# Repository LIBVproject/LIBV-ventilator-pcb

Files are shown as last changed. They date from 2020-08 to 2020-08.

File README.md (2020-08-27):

# LIBV Open Source Ventilator

Check out our [www.bvmvent.org](https://www.bvmvent.org/) for updates.

**The Problem:** The COVID-19 Pandemic has highlighted the scarcity of potentially life-saving resources around the world.

**Our Challenge:** Design and Engineer an Open Source, low cost (sub $150) ventilator using readily available materials for rapid deployment in developing countries where there may not be an alternative.

Who we are: A Collective of Engineers, Medics and Scientists from across the world, centred around a hub in Phnom Penh, Cambodia.
Help Us: We need Volunteers, a Community of Contributors and Donors to join us and help us deliver our vision.

## Arduino Program

Check out our [Arduino Program](https://github.com/LIBVproject/LIBV-ventilator).

## Electronics PCB

The LIBV electronics are based on an Arduino Nano (Atmega328) architecture.

### Circuit Digram

<p align="center">
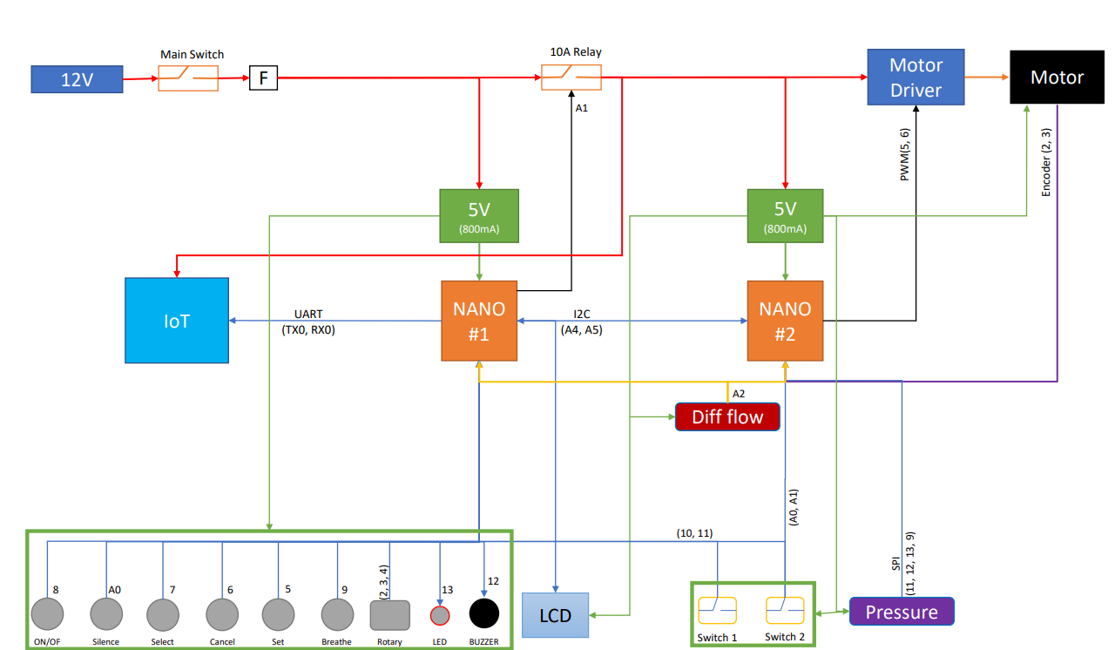
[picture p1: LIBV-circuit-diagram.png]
  
</p>

### Printed PCB

<p align="center">
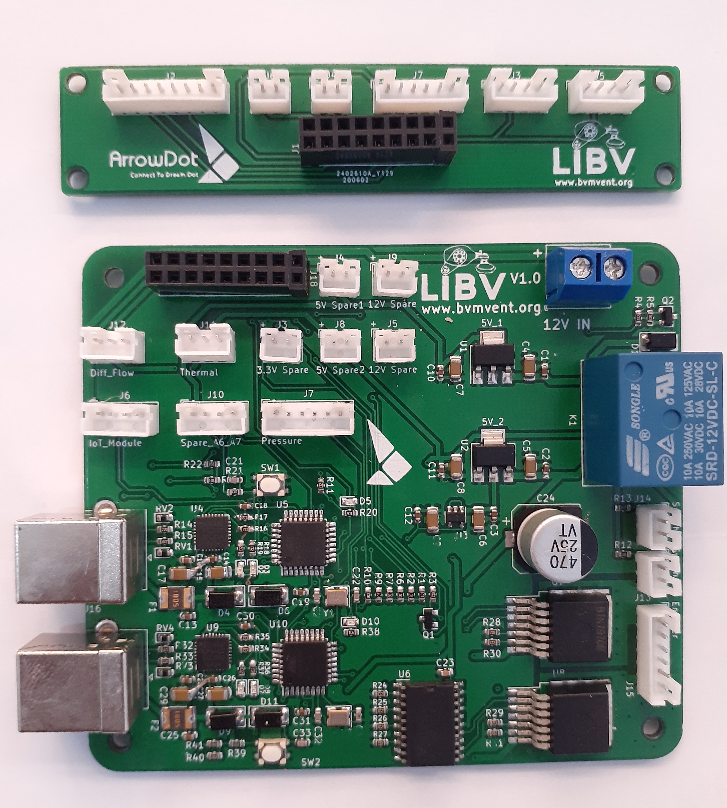
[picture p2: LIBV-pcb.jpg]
  
</p>

<p align="center">
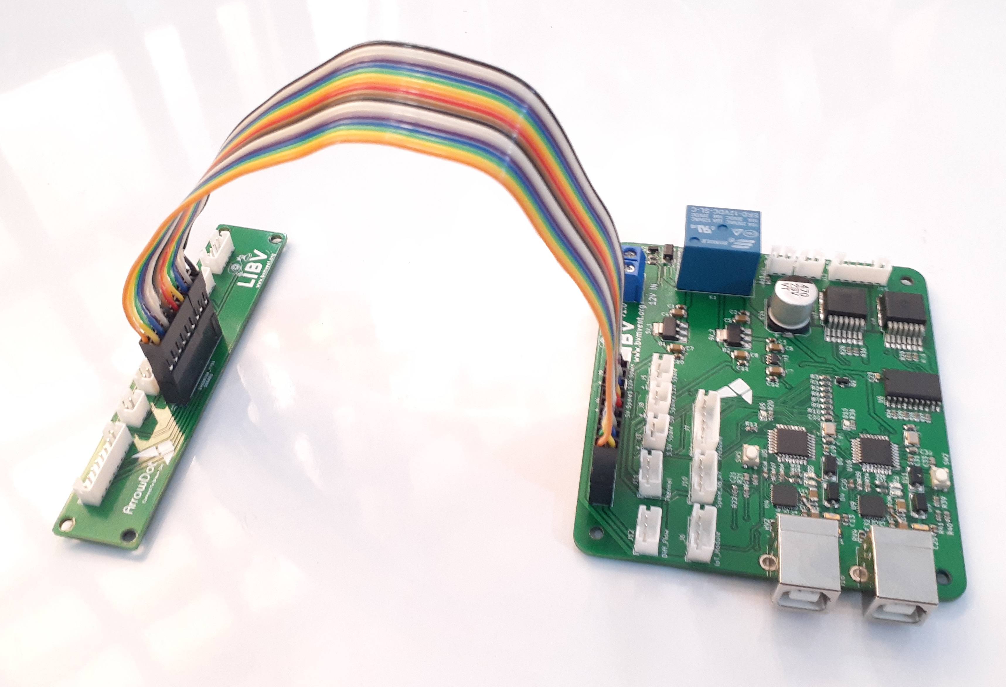
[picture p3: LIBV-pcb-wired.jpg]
  
</p>

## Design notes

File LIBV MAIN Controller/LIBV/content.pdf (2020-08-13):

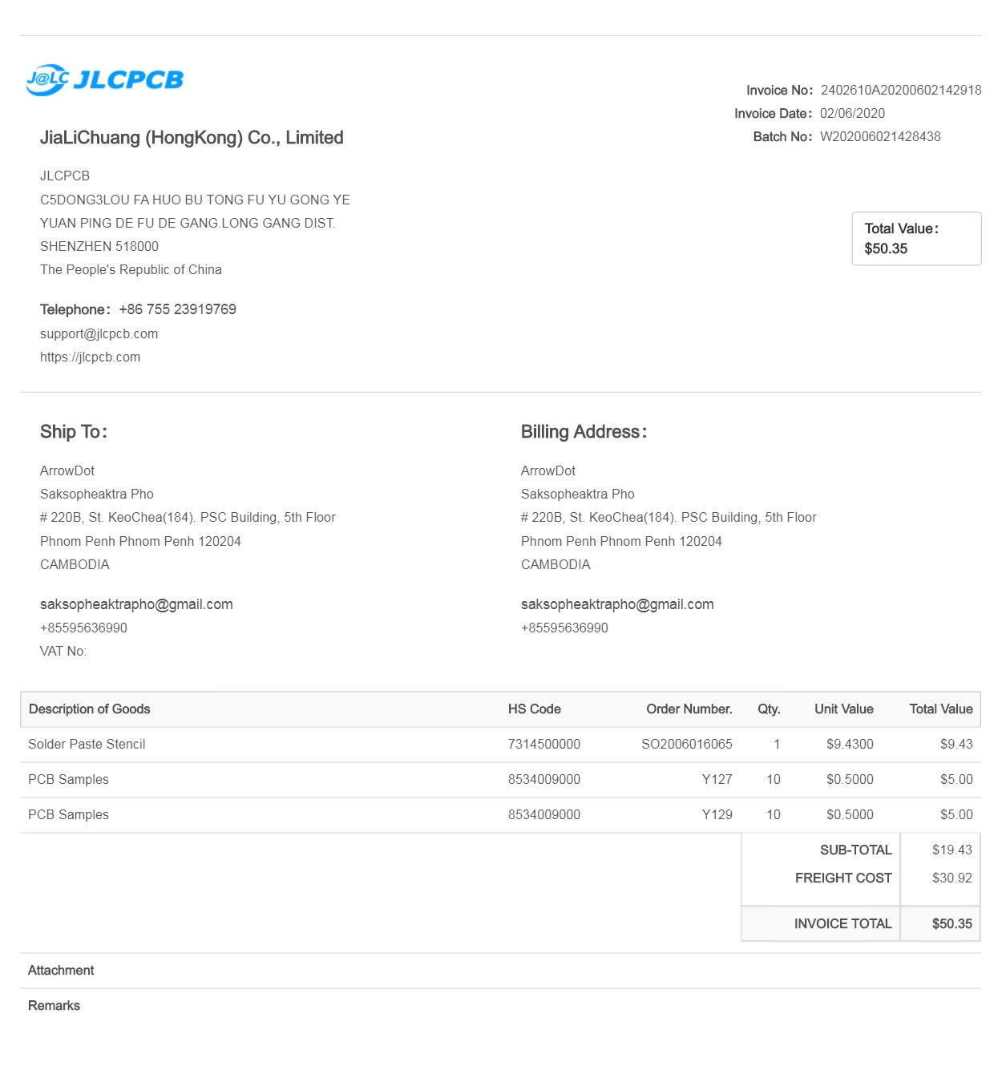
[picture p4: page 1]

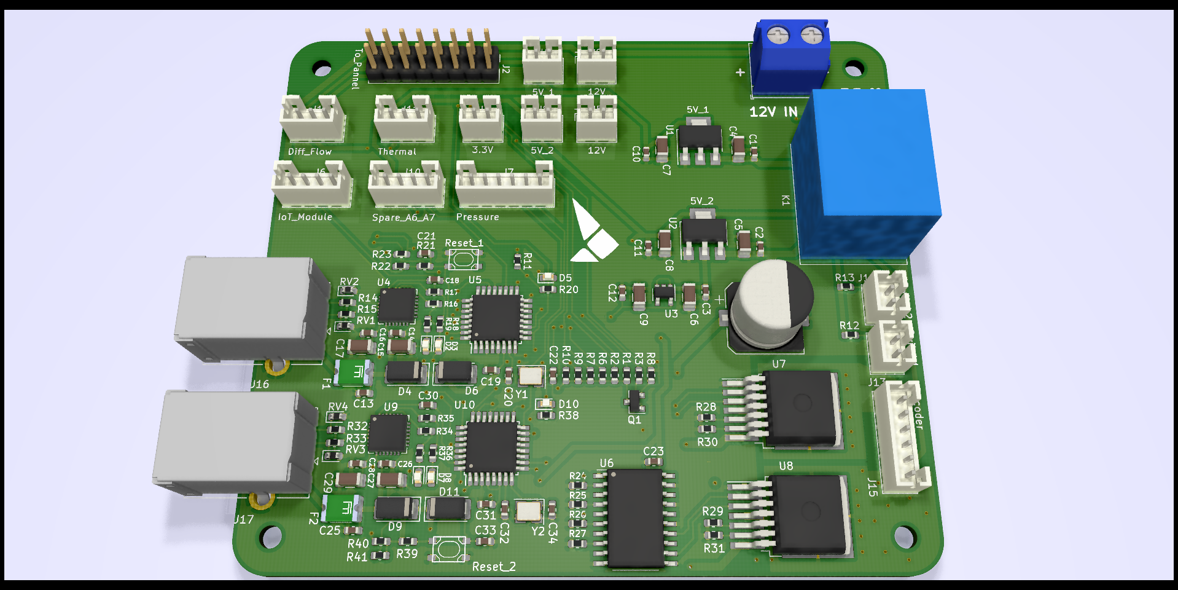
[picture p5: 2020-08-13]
LIBV MAIN Controller/LIBV/3D_Image/LIBV_2.png

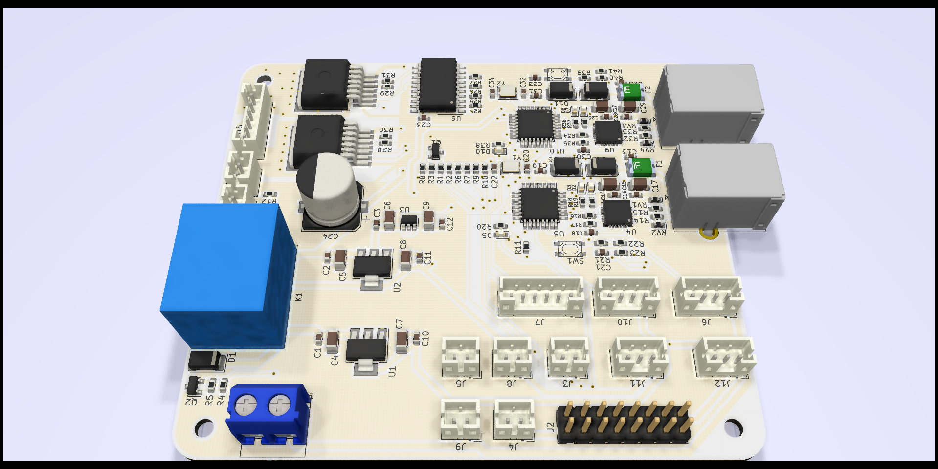
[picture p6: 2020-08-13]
LIBV MAIN Controller/LIBV/3D_Image/LIBV.png

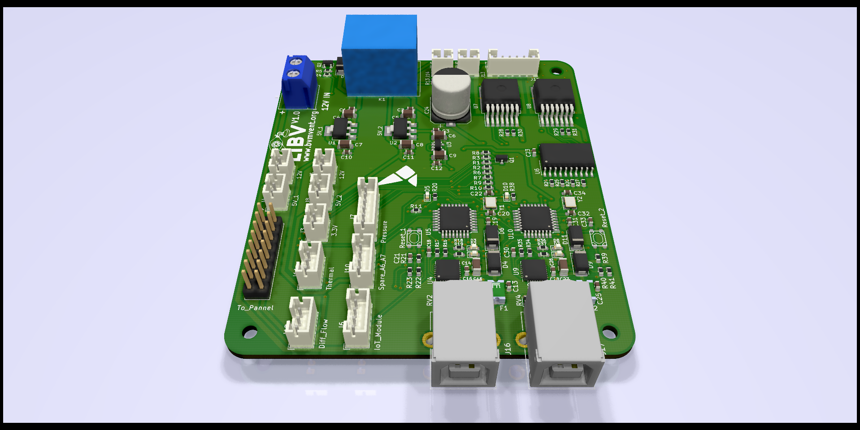
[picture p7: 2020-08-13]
LIBV MAIN Controller/LIBV/3D_Image/New folder/LIBV_.png

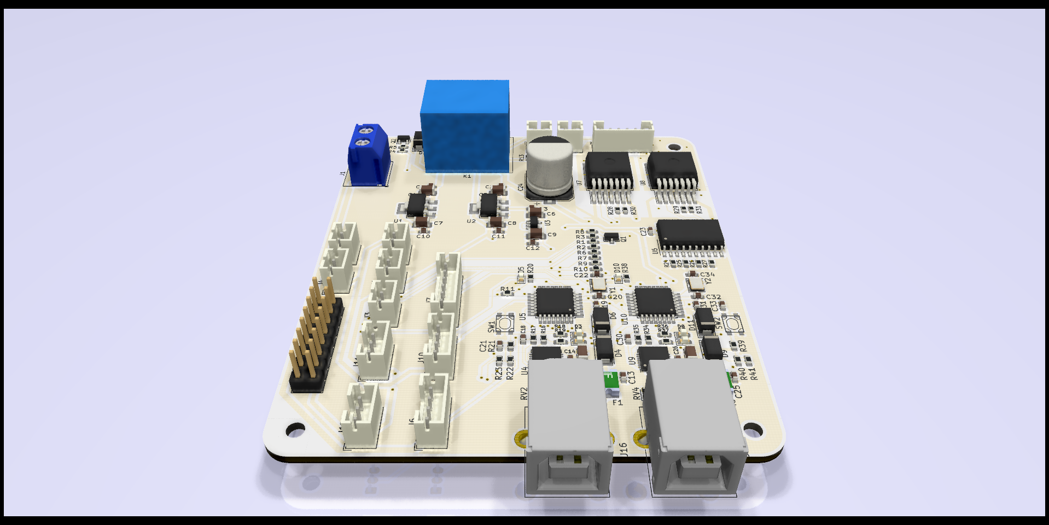
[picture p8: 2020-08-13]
LIBV MAIN Controller/LIBV/3D_Image/LIBV2.png

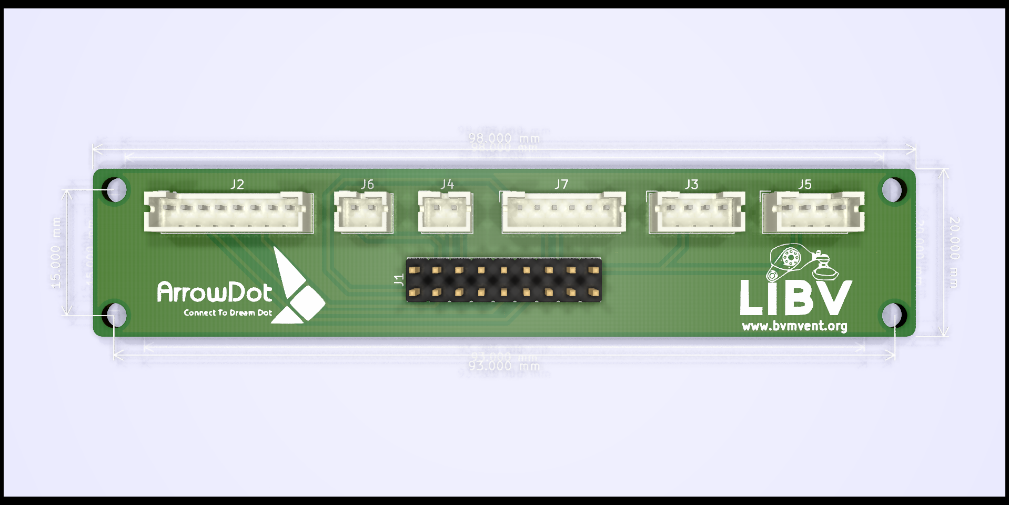
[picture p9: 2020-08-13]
LIBV_Pannel/LIBV_Pannel.png

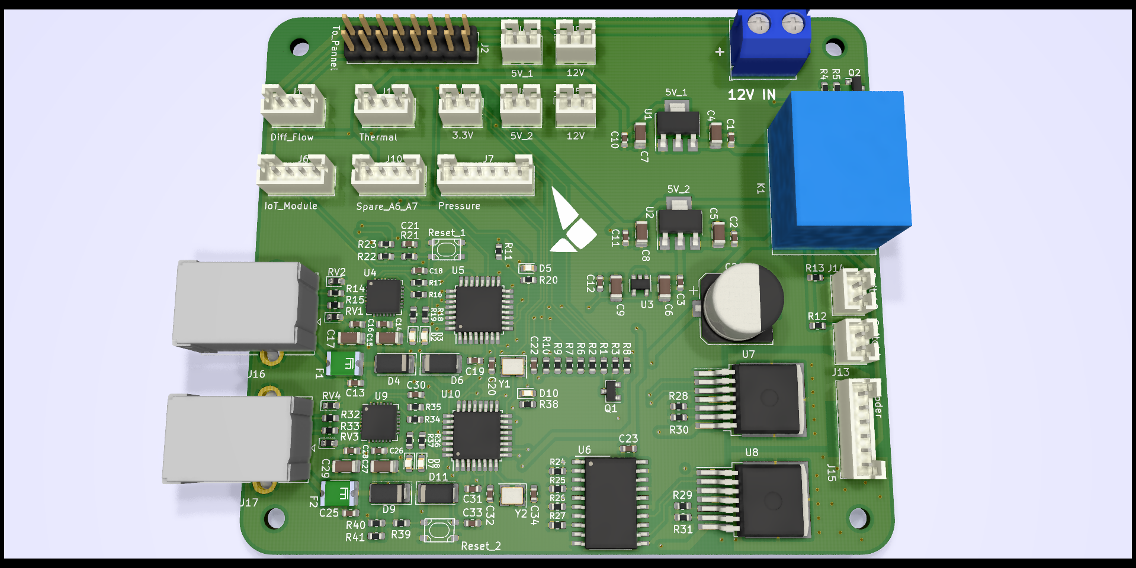
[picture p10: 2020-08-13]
LIBV MAIN Controller/LIBV/3D_Image/LIBV_.png

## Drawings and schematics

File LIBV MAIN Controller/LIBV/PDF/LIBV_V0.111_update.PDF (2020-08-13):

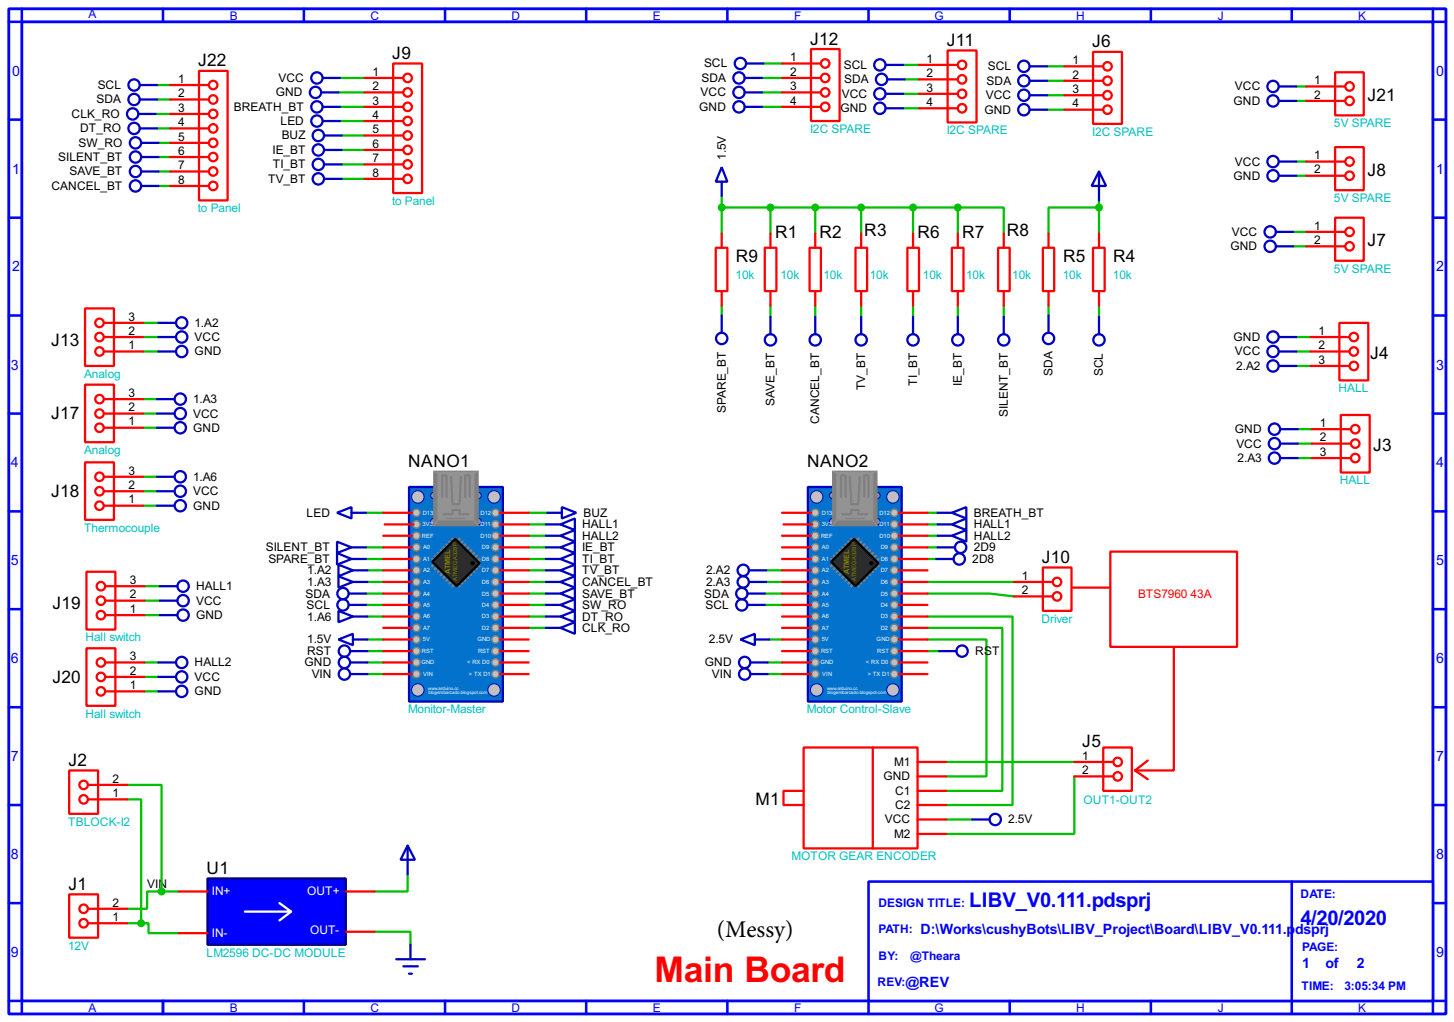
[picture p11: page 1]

NANO1
www.arduino.cc blogembarcado.blogspot.com ATMEGA328P ATMEL

NANO2

DESIGN TITLE: LIBV_V0.111.pdsprj VIN

9 PATH: D:\Works\cushyBots\LIBV_Project\Board\LIBV_V0.111.pdsprj

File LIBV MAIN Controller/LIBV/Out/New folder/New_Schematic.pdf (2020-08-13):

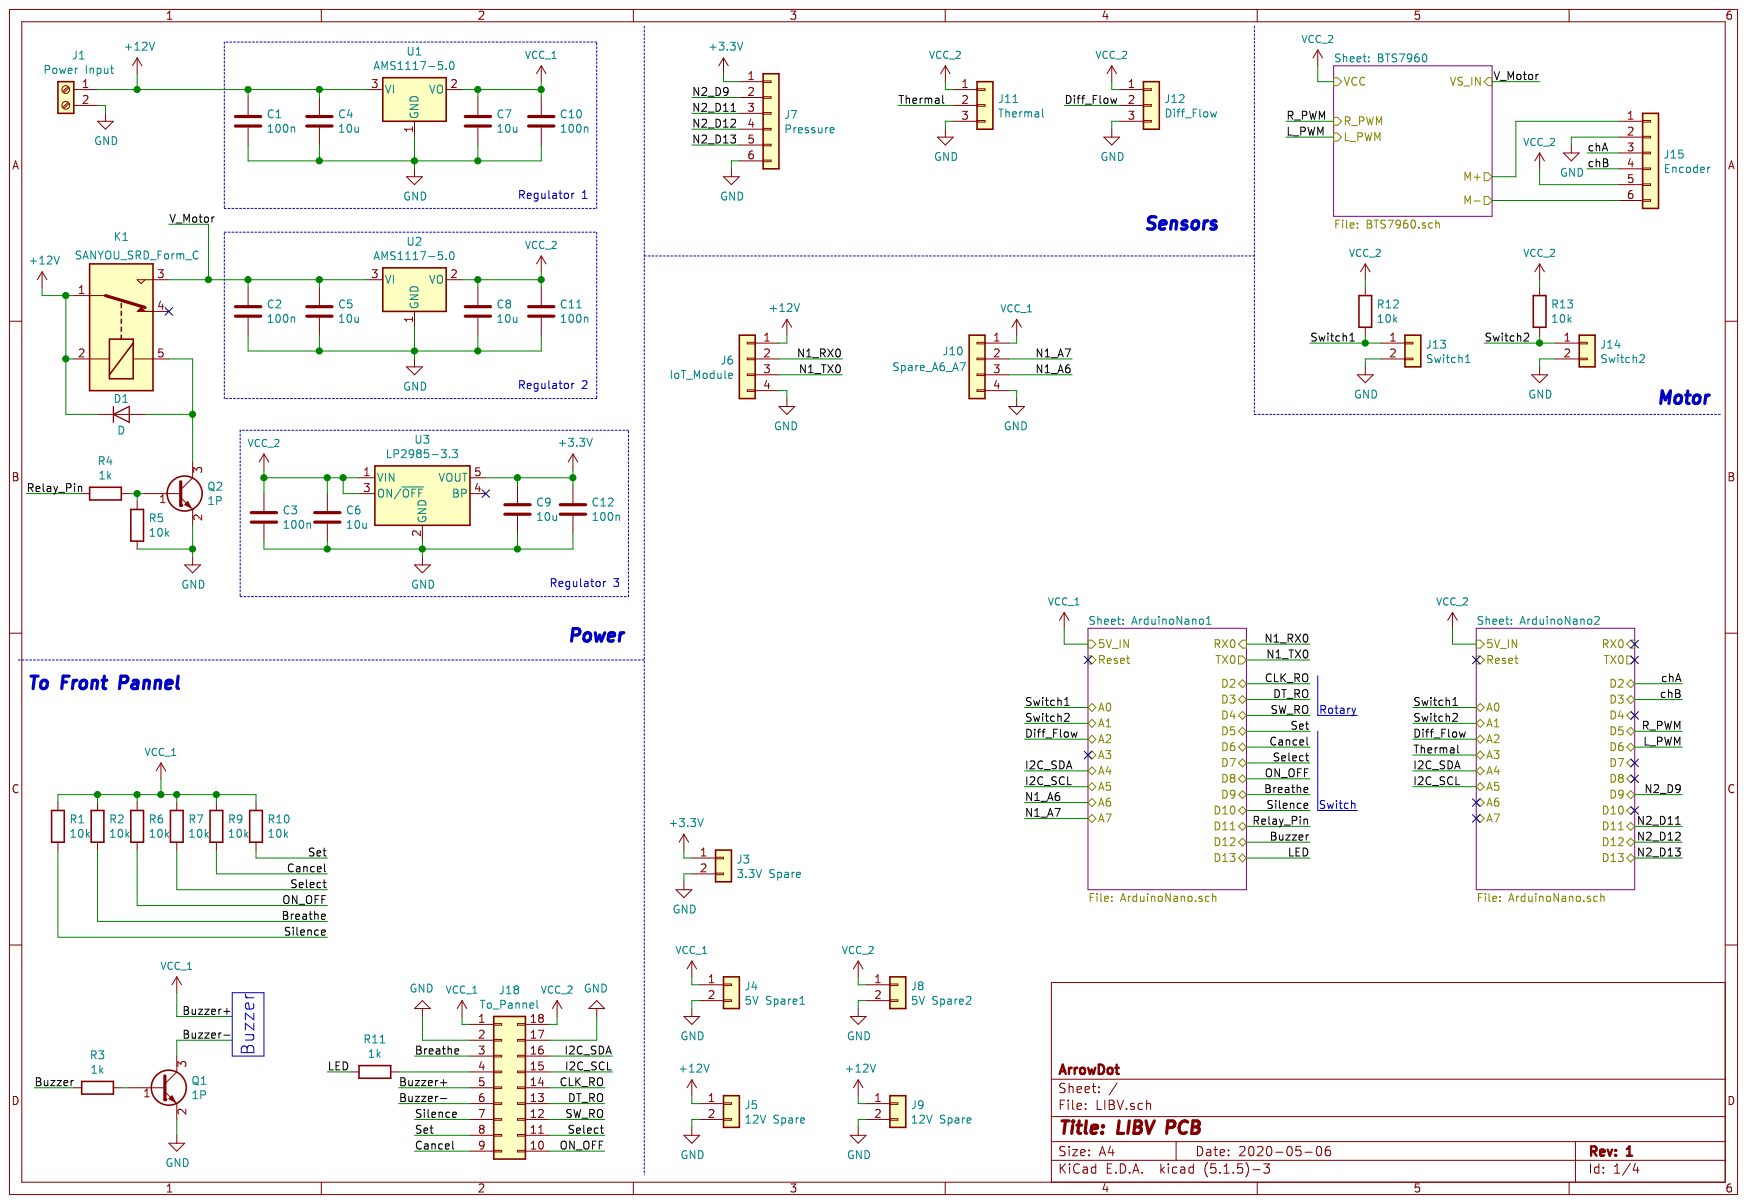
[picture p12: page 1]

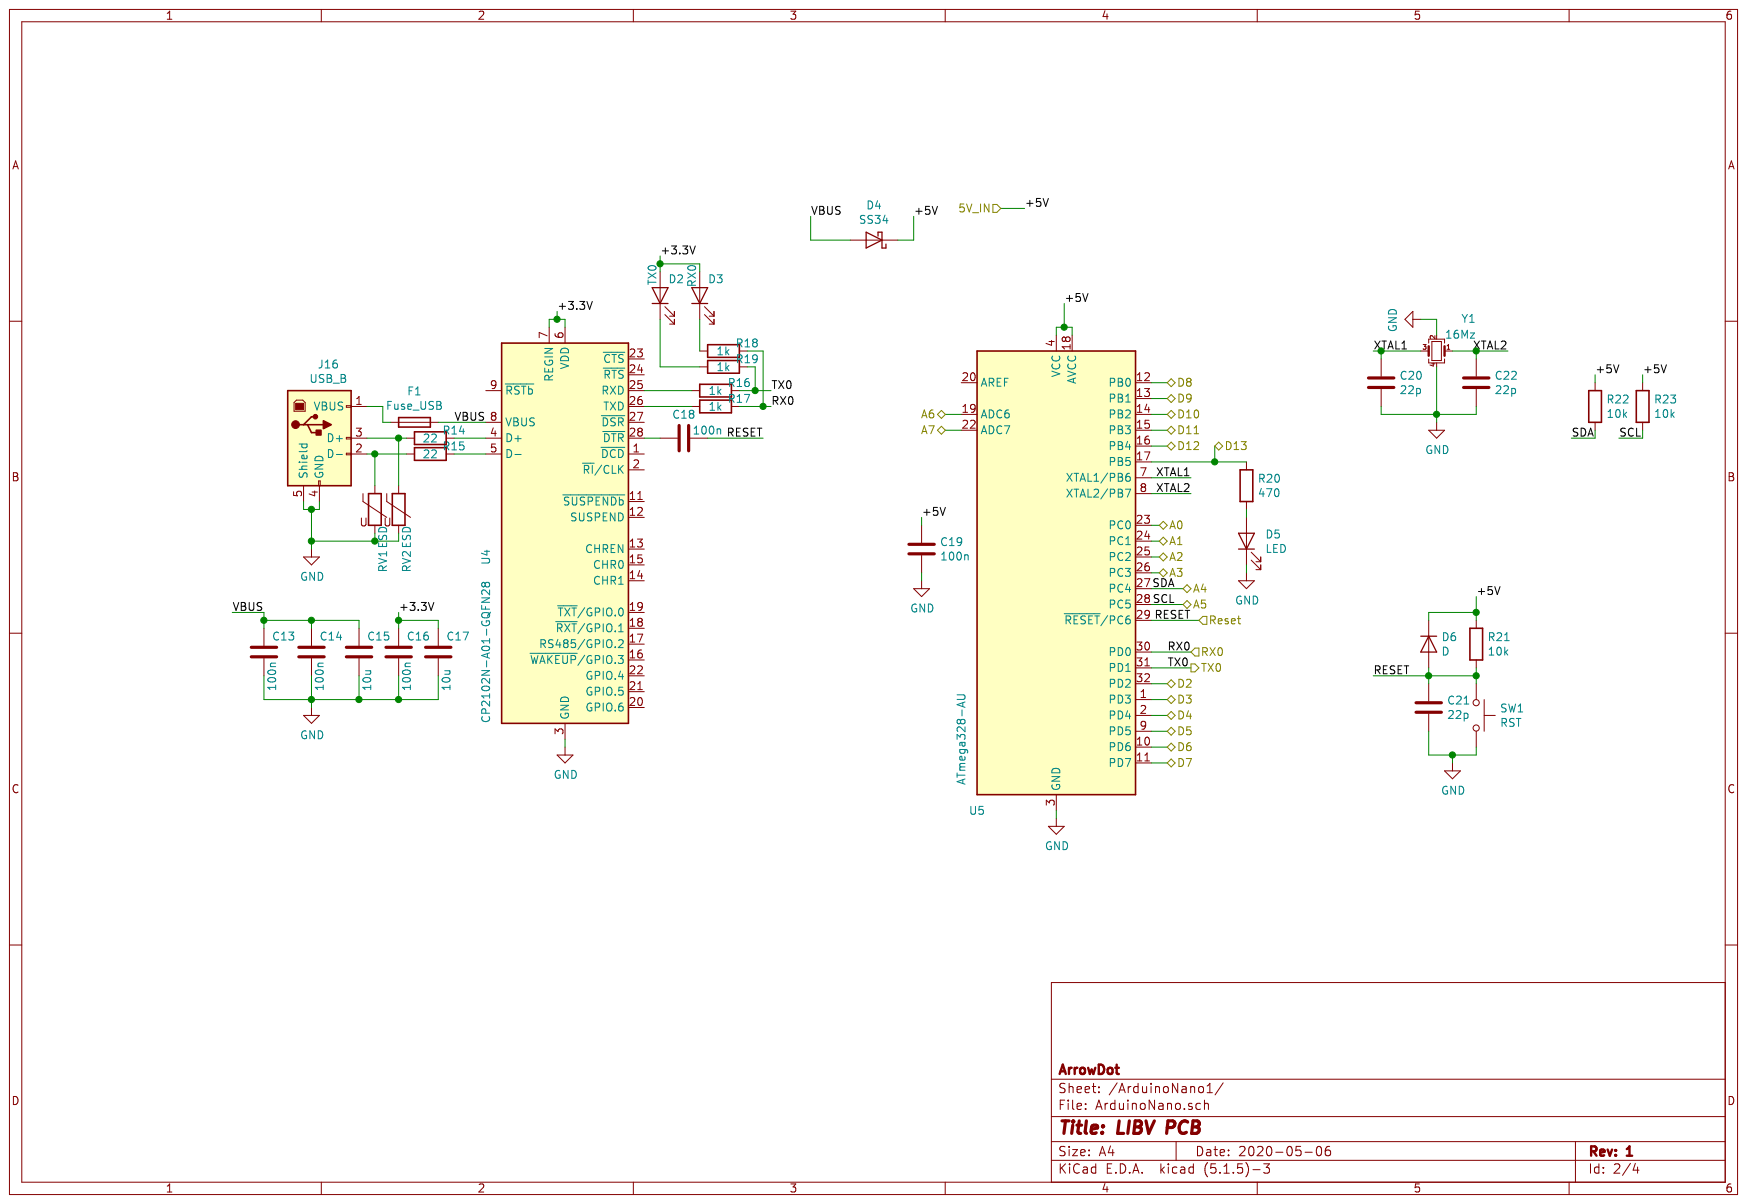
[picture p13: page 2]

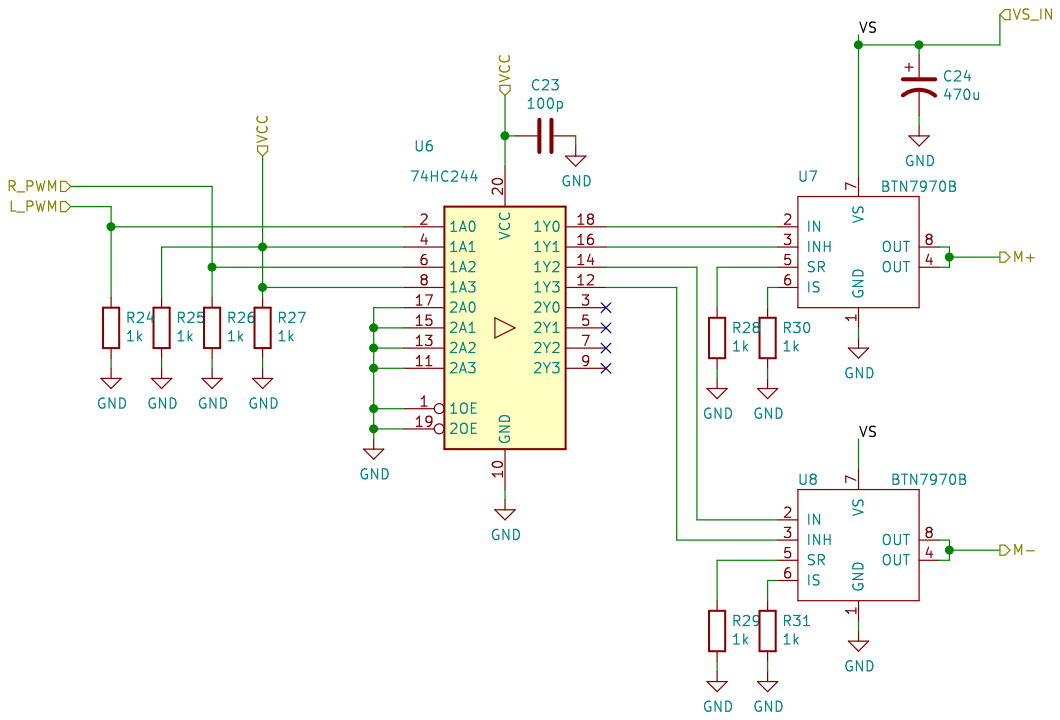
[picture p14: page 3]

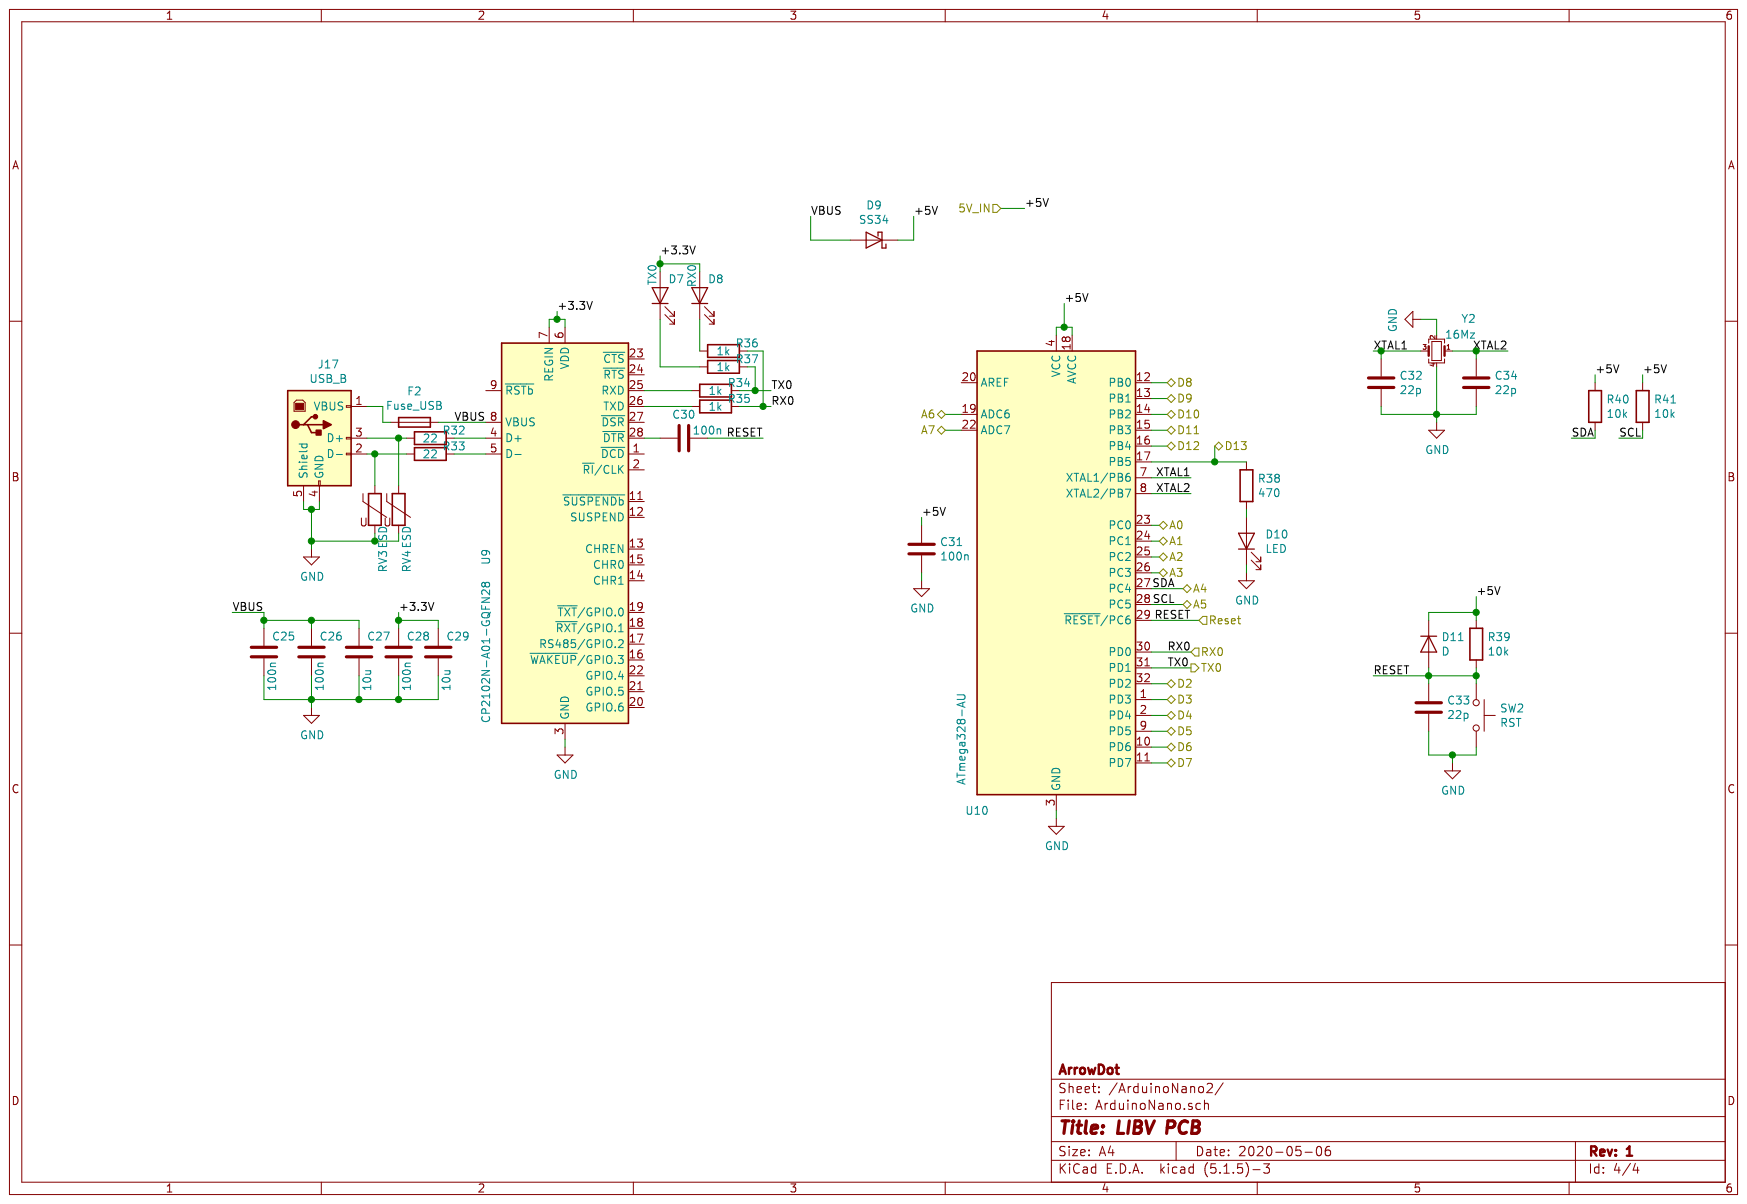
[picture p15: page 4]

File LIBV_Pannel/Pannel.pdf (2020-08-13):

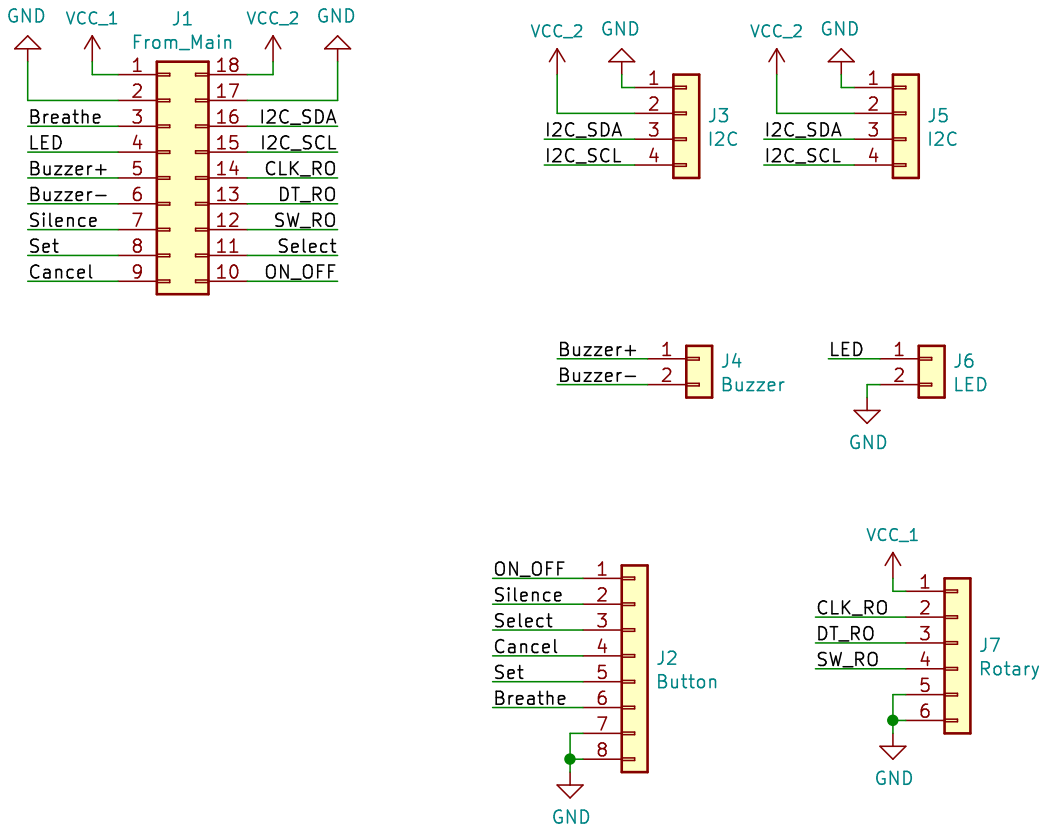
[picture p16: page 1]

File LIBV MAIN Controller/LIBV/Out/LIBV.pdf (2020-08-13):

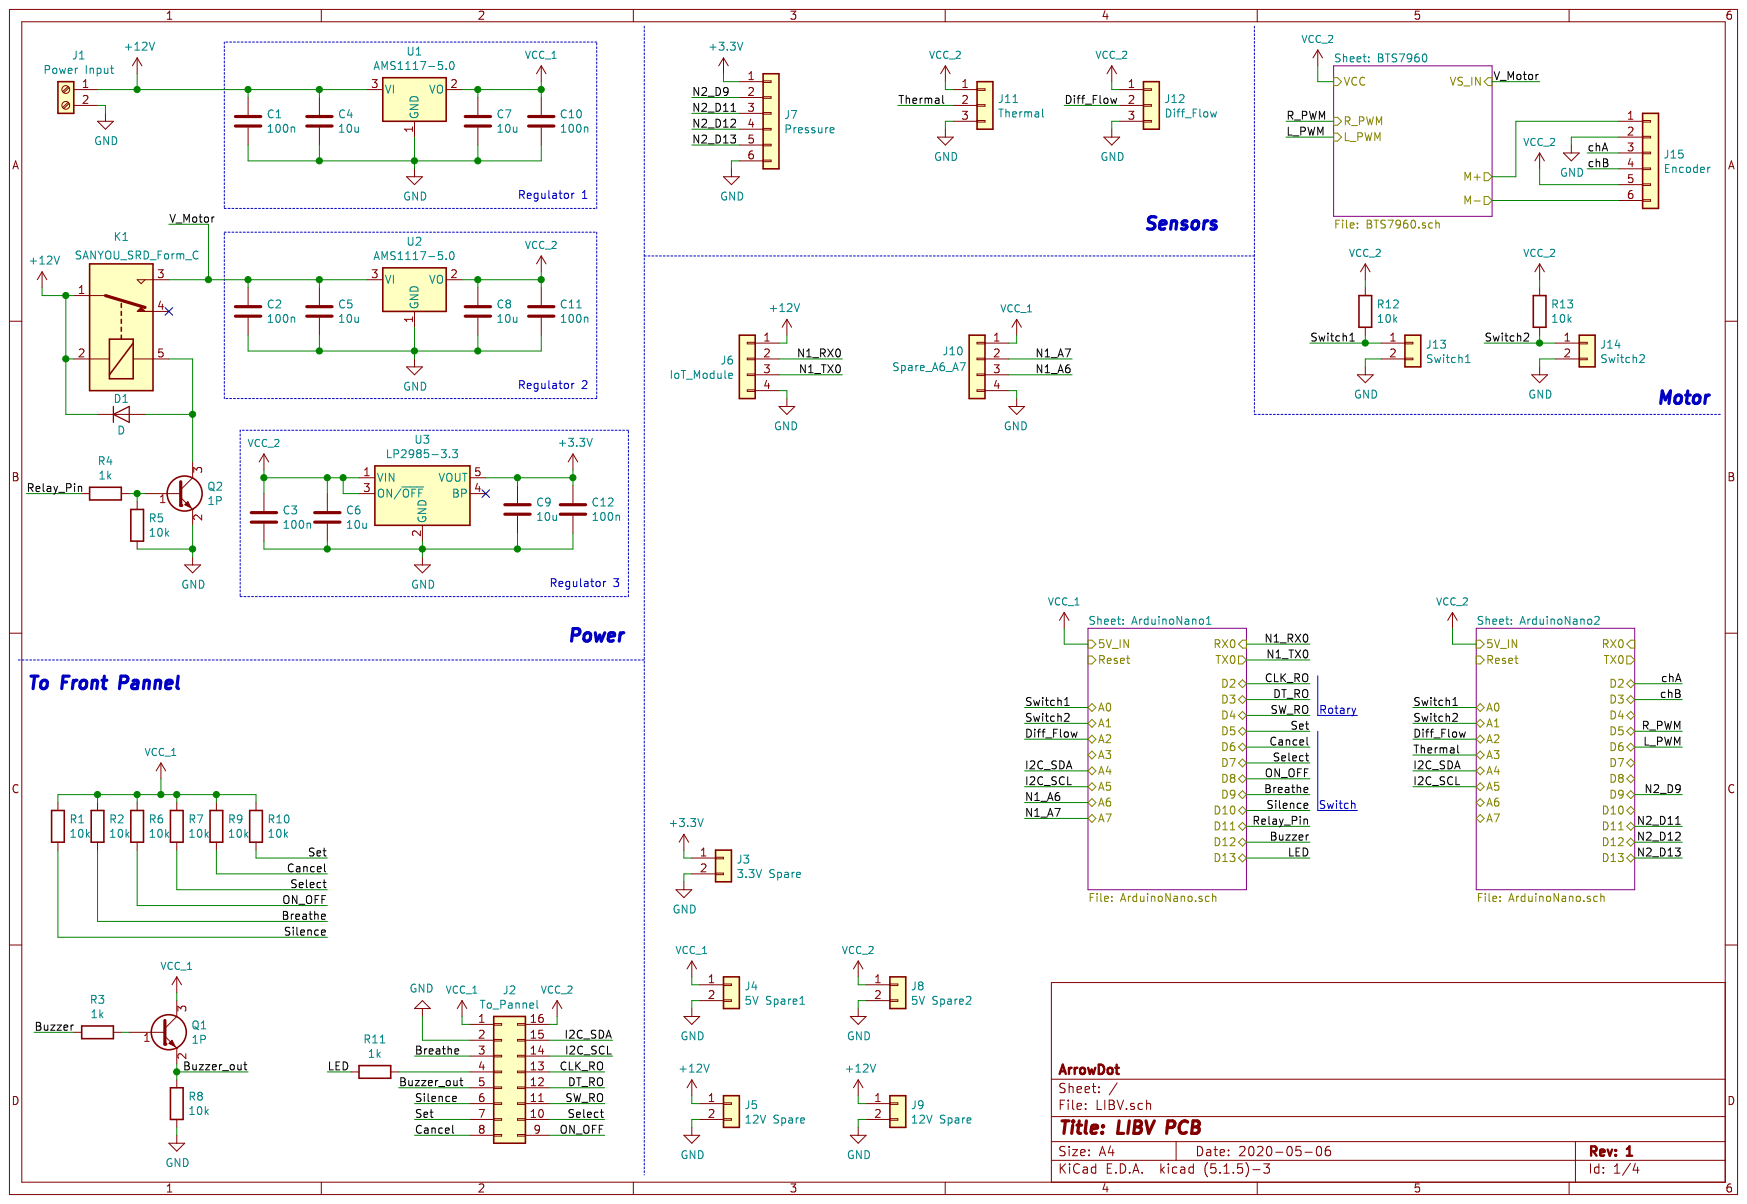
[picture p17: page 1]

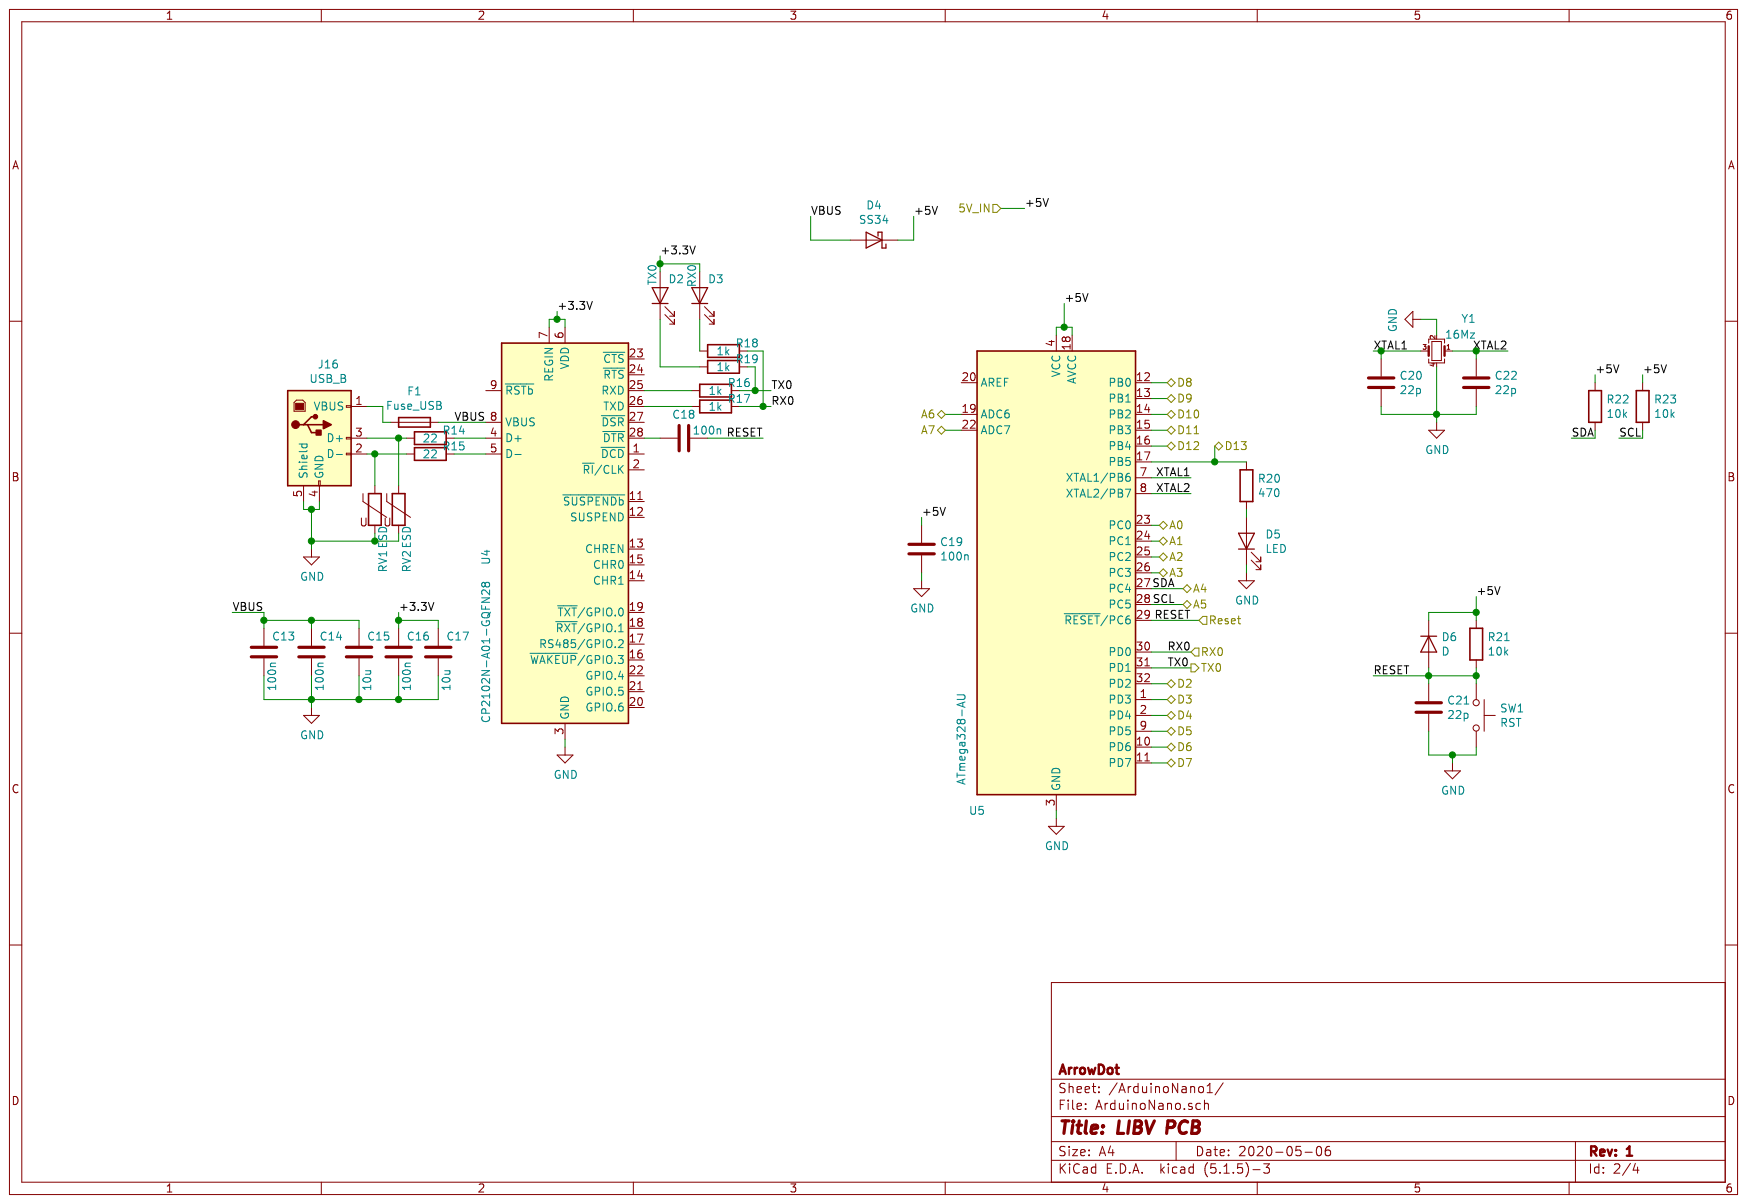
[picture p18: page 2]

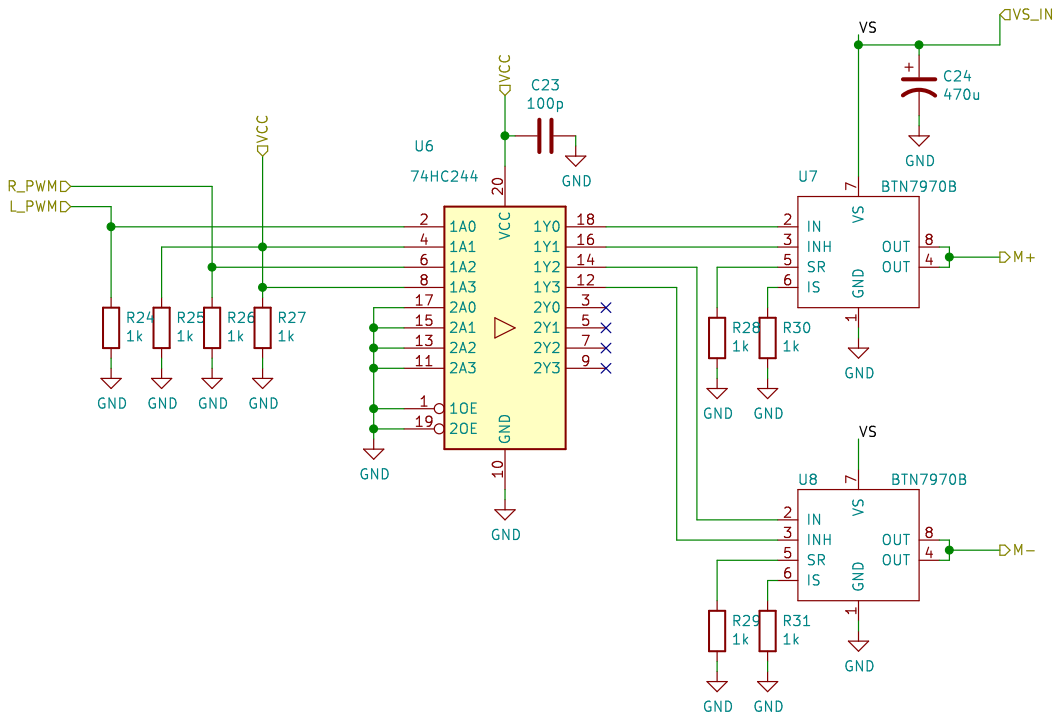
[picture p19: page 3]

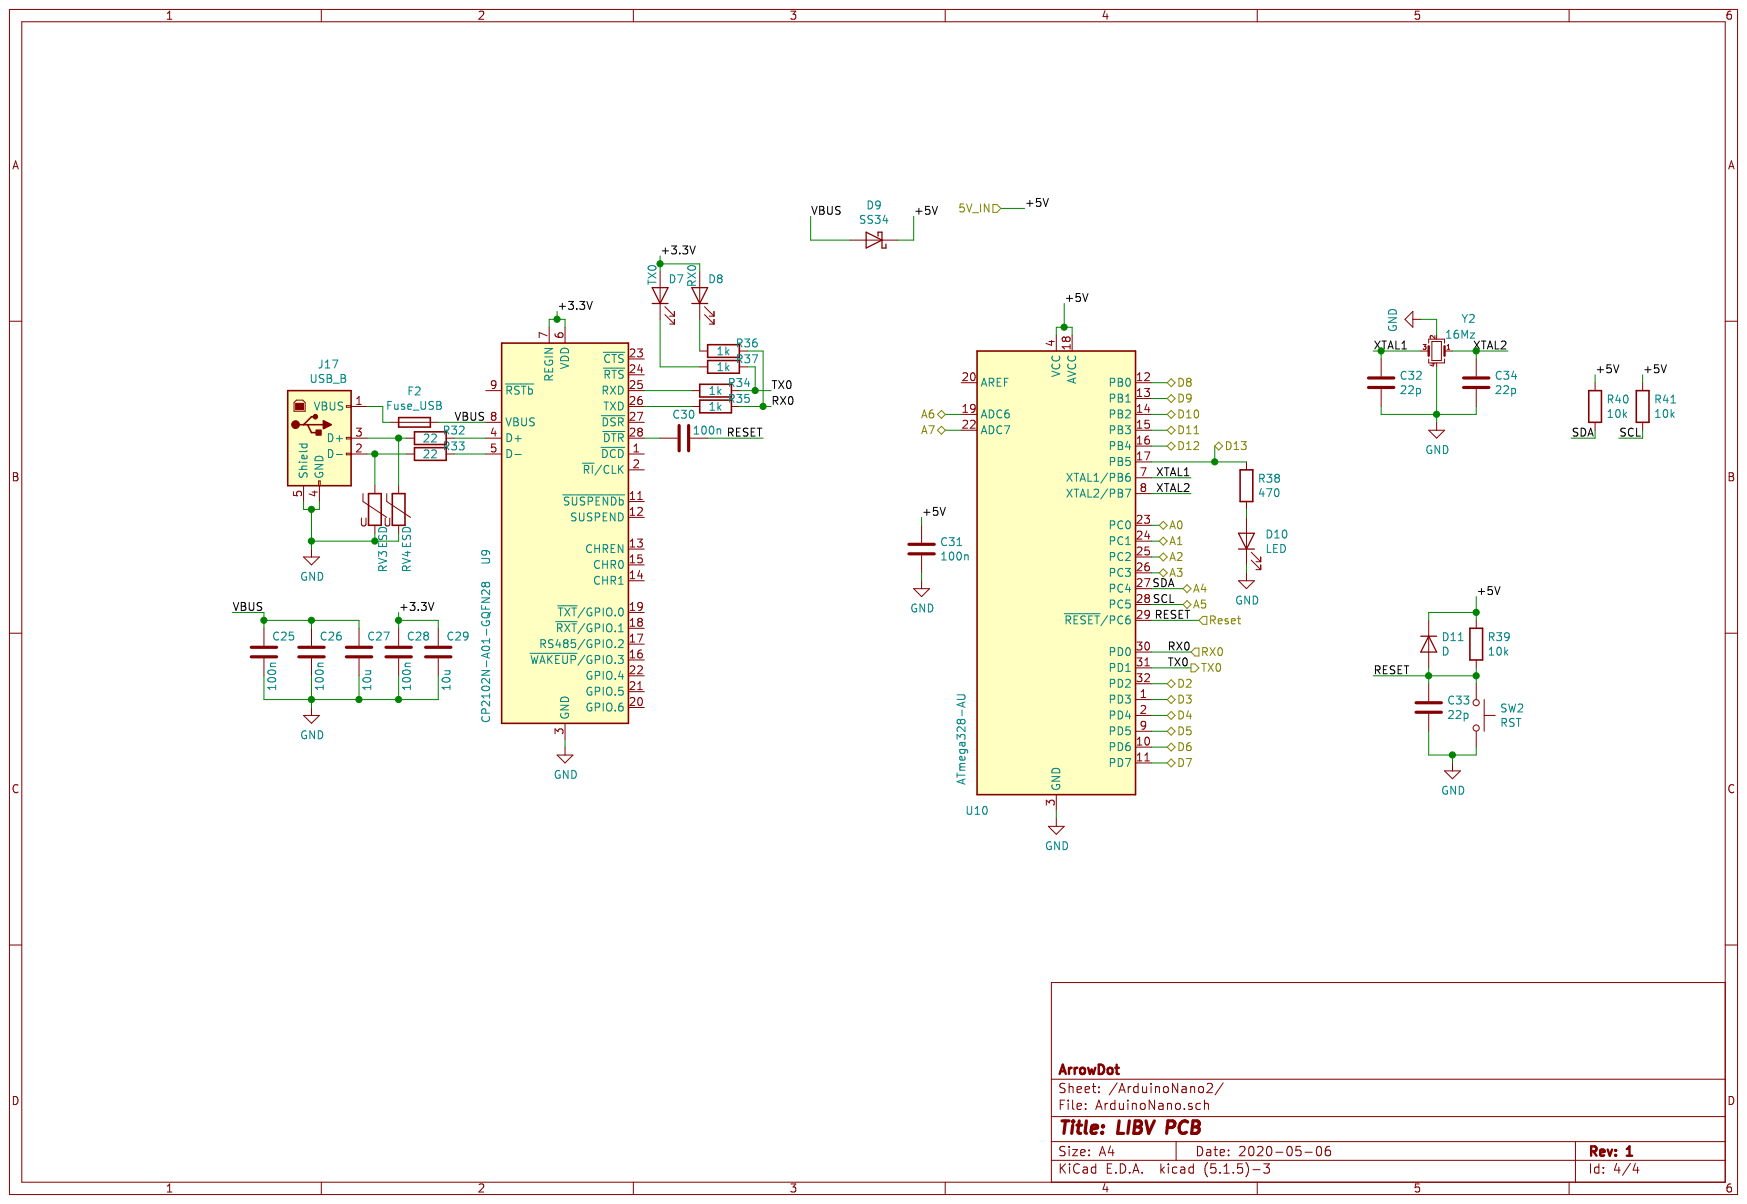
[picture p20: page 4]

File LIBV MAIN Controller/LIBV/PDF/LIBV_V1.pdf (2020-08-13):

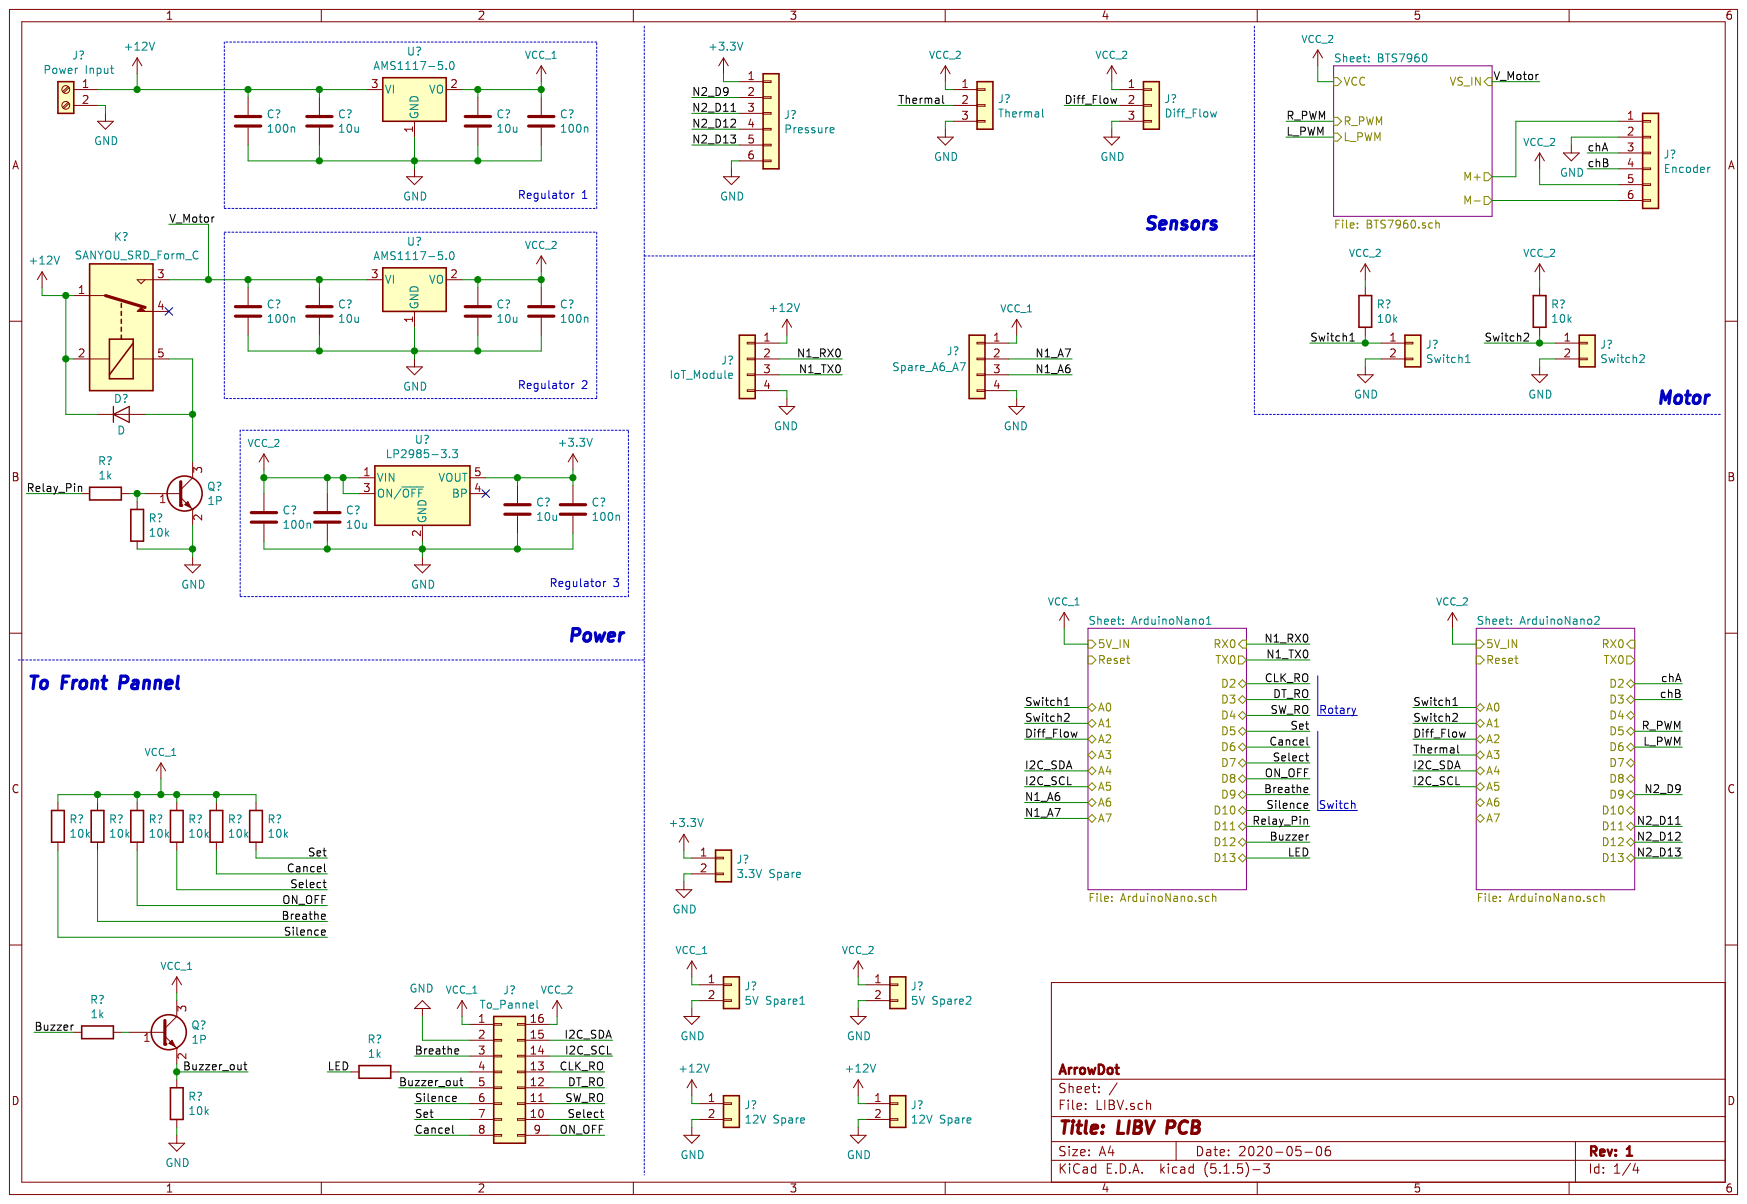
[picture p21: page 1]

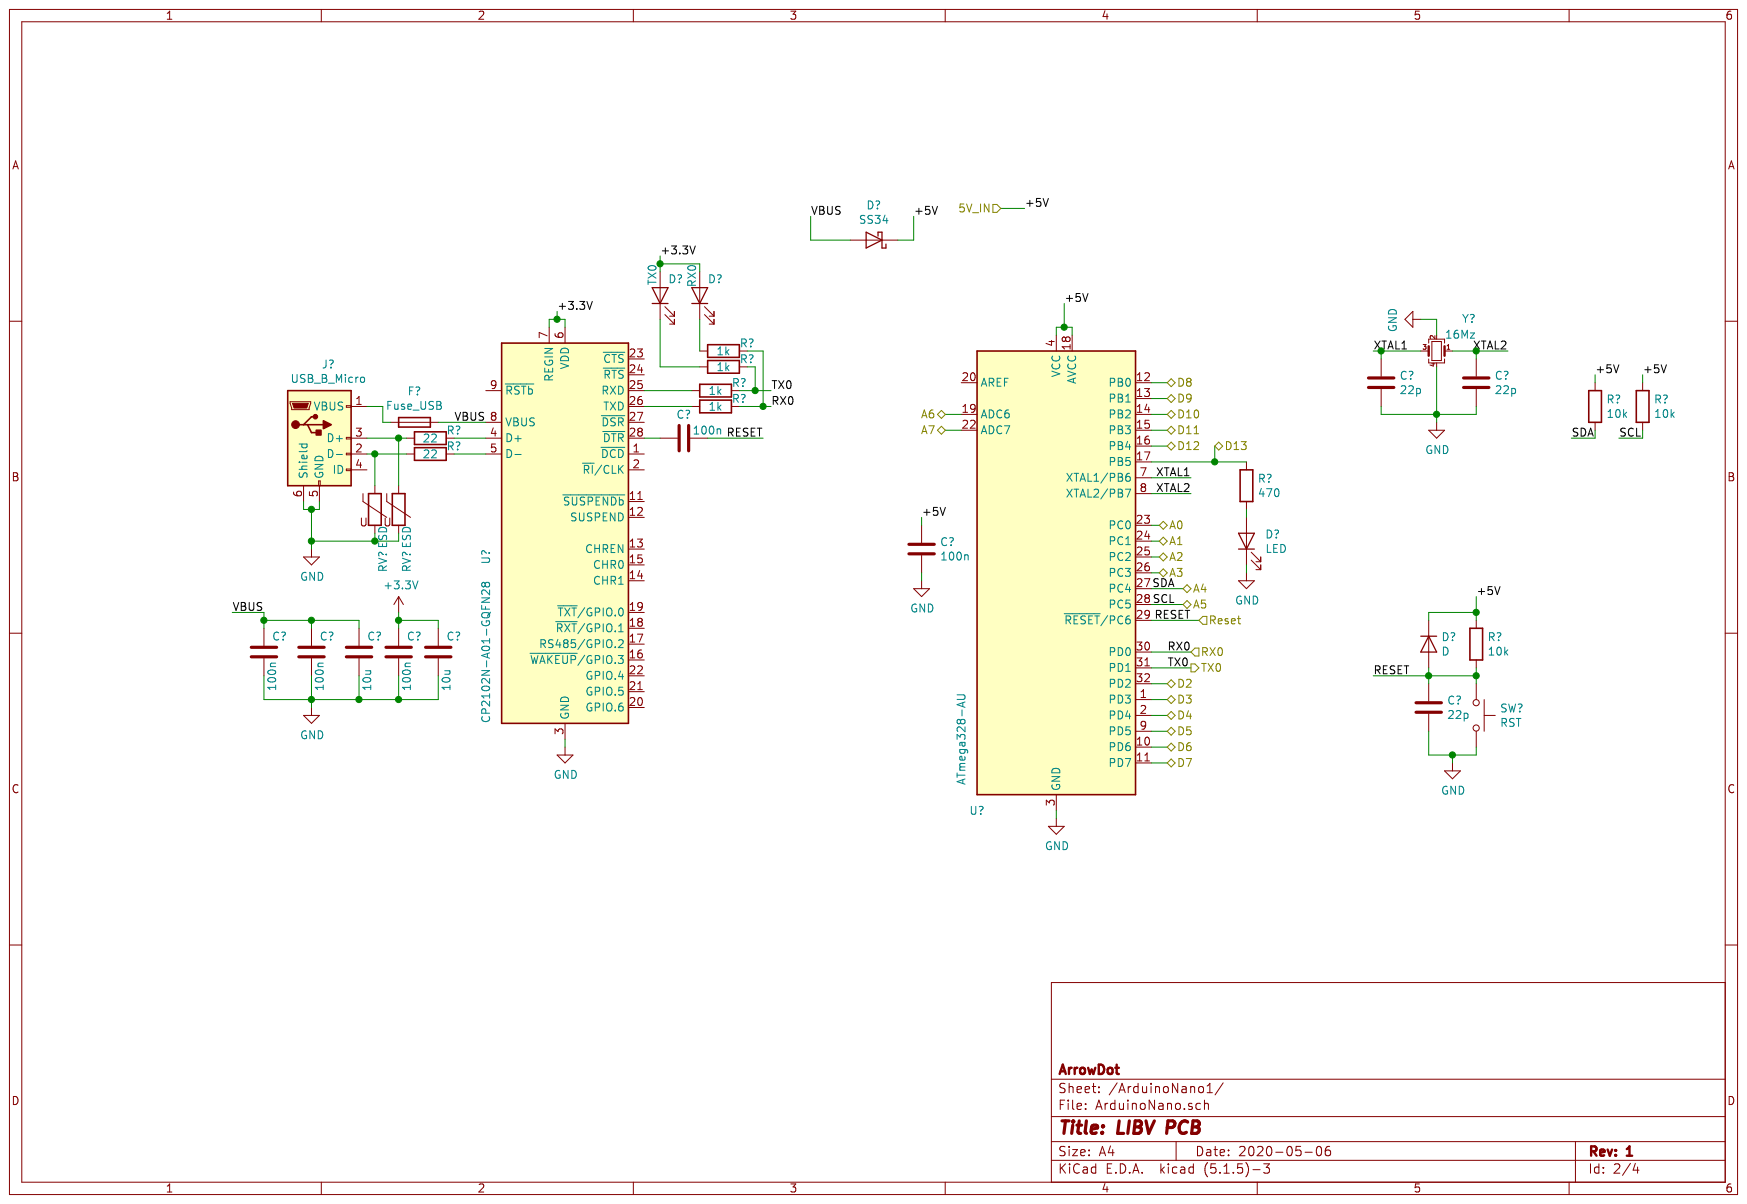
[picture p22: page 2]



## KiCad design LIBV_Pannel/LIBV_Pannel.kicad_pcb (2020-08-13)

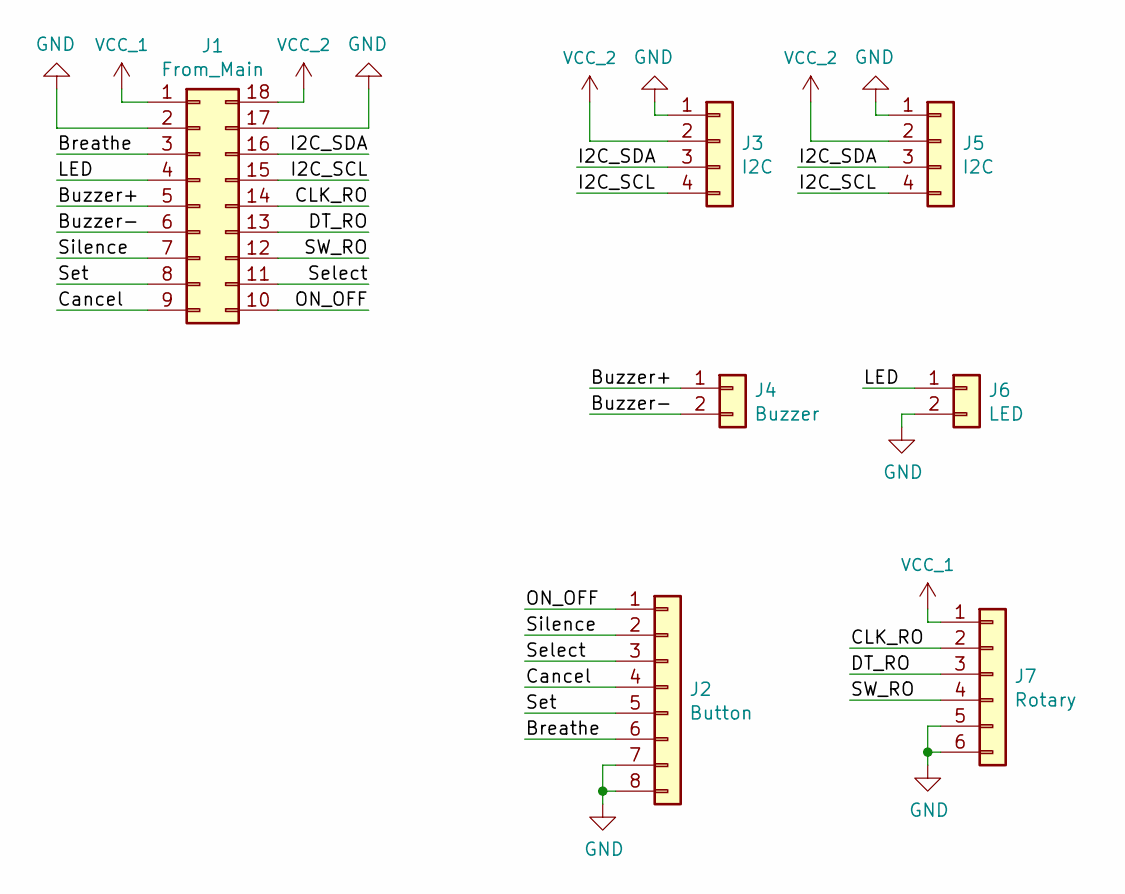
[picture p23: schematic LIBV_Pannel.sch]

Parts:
J1: From_Main; PinHeader_2x09_P2.54mm_Vertical
J2: Button; JST_PH_B8B-PH-K_1x08_P2.00mm_Vertical
J3, J5: I2C; JST_PH_B4B-PH-K_1x04_P2.00mm_Vertical
J4: Buzzer; JST_PH_B2B-PH-K_1x02_P2.00mm_Vertical
J6: LED; JST_PH_B2B-PH-K_1x02_P2.00mm_Vertical
J7: Rotary; JST_PH_B6B-PH-K_1x06_P2.00mm_Vertical

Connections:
/Breathe: J1.3, J2.6
/Buzzer+: J1.5, J4.1
/Buzzer-: J1.6, J4.2
/CLK_RO: J1.14, J7.2
/Cancel: J1.9, J2.4
/DT_RO: J1.13, J7.3
/I2C_SCL: J1.15, J3.4, J5.4
/I2C_SDA: J1.16, J3.3, J5.3
/LED: J1.4, J6.1
/ON_OFF: J1.10, J2.1
/SW_RO: J1.12, J7.4
/Select: J1.11, J2.3
/Set: J1.8, J2.5
/Silence: J1.7, J2.2
GND: J1.2, J1.17, J2.7, J2.8, J3.1, J5.1, J6.2, J7.5, J7.6
VCC_1: J1.1, J7.1
VCC_2: J1.18, J3.2, J5.2

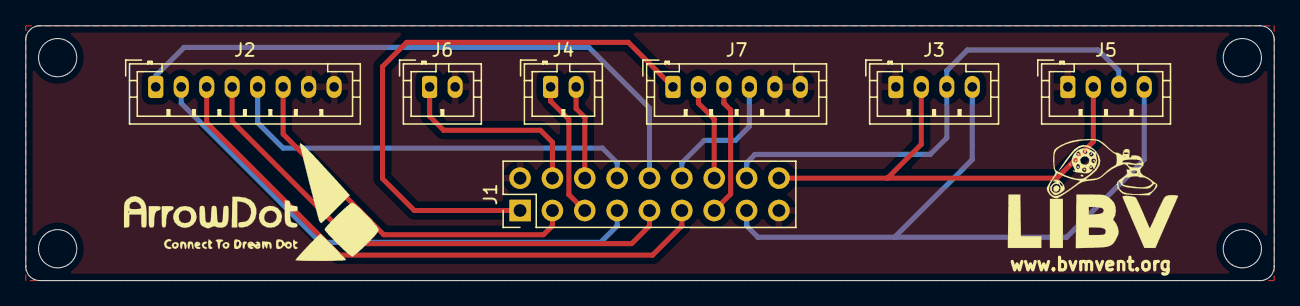
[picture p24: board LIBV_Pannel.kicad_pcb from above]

Board: 2 copper layers, 98.0 x 20.0 mm, 7 parts (0 on the bottom side), 17 nets.

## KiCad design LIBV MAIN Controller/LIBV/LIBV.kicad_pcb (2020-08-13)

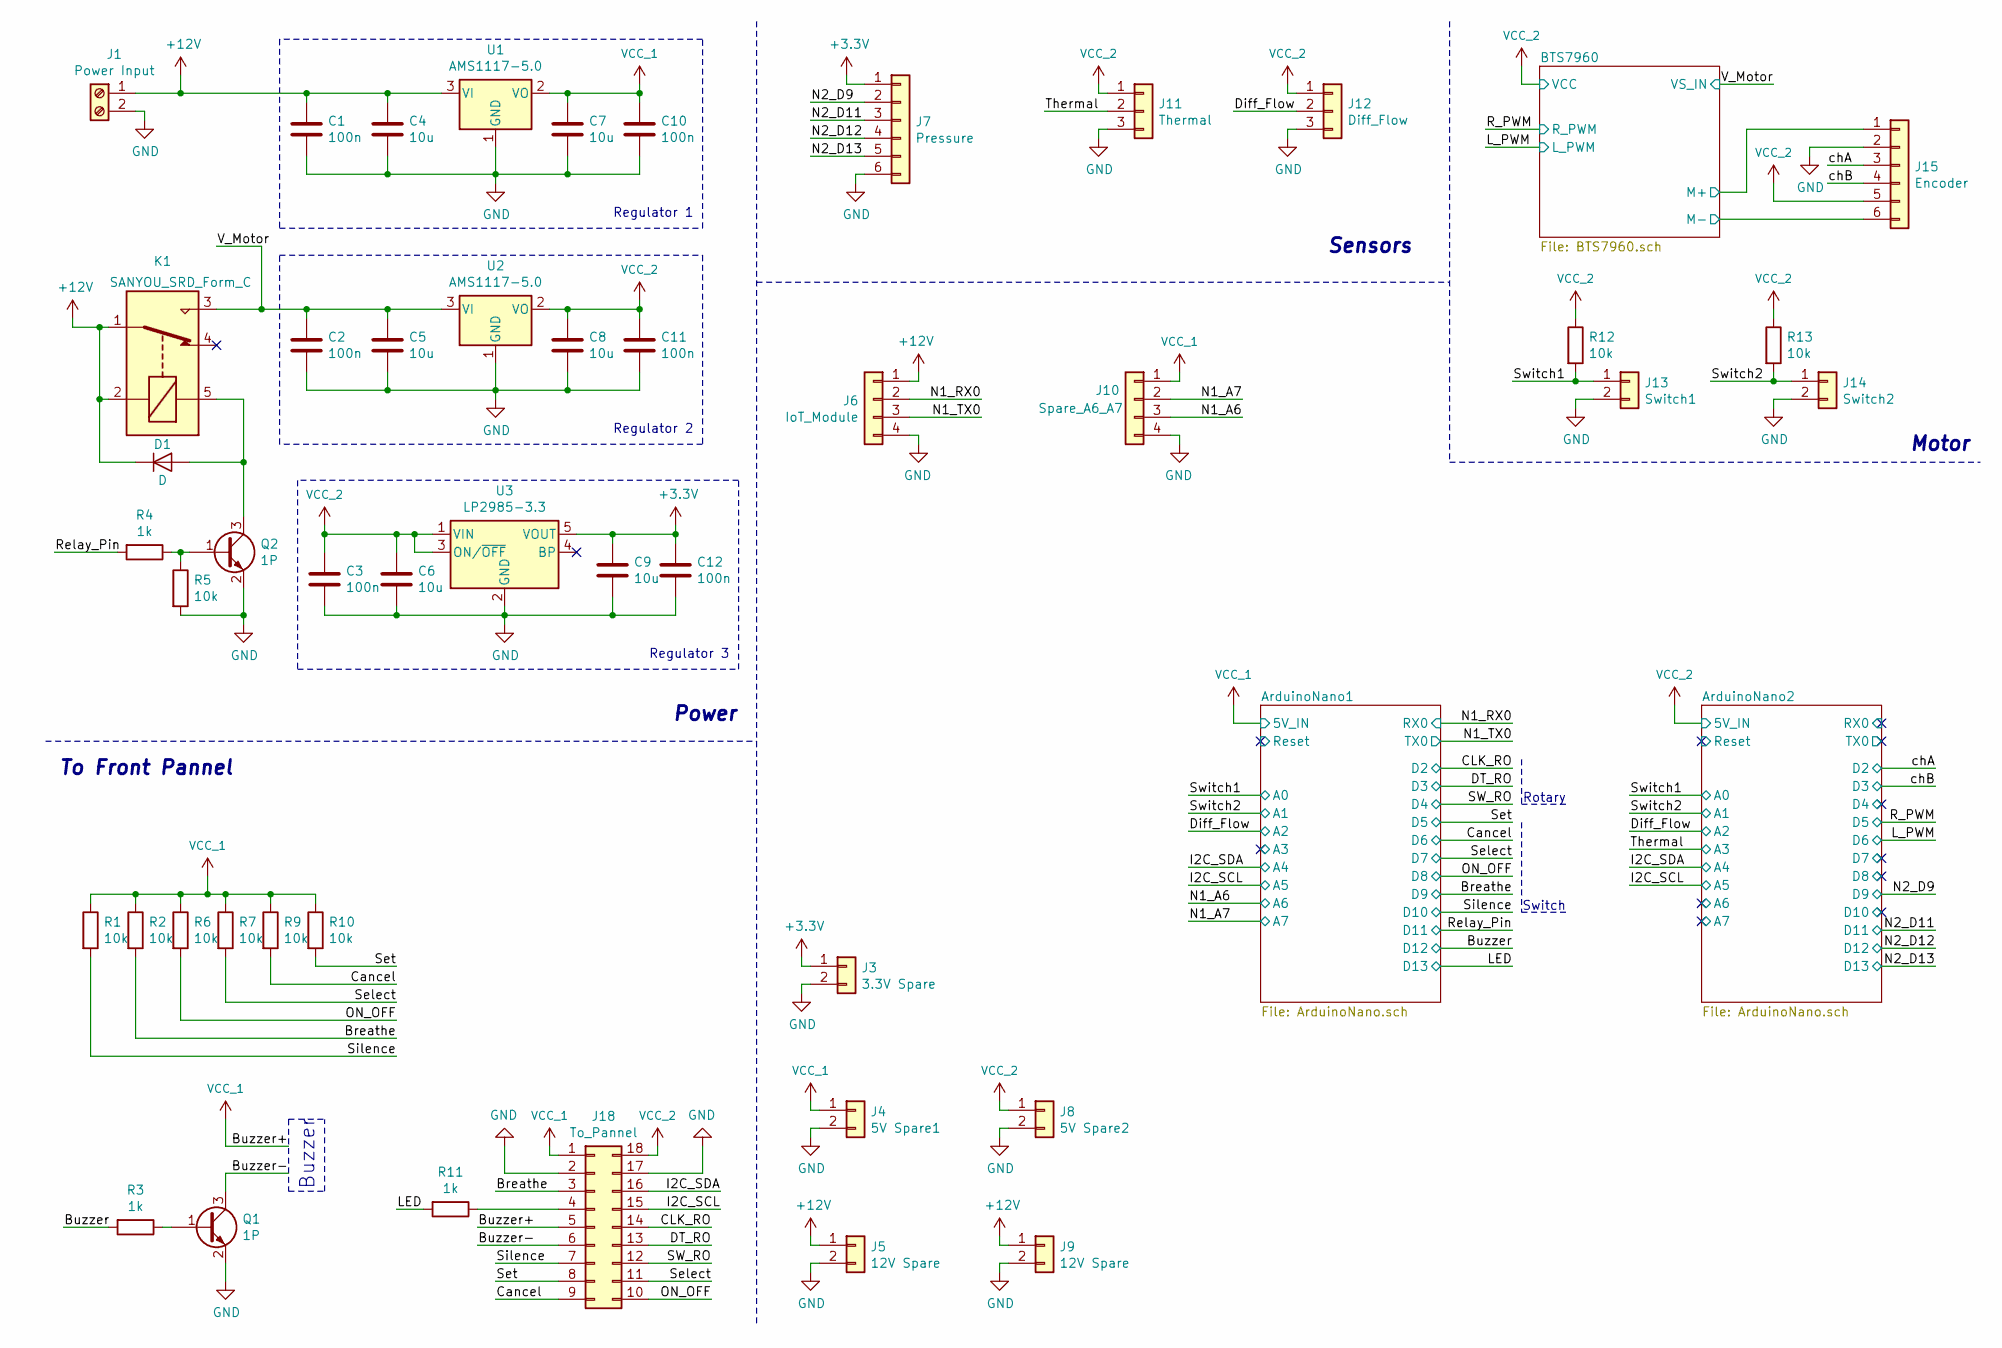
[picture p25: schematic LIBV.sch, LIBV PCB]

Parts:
C1, C2, C3, C10, C11, C12: 100n; C_0603_1608Metric
C4, C5, C6, C7, C8, C9: 10u; C_1206_3216Metric
D1: D; D_2010_5025Metric
J1: Power Input; TerminalBlock_Phoenix_MKDS-1,5-2_1x02_P5.00mm_Horizontal
J3: 3.3V Spare; JST_PH_B2B-PH-K_1x02_P2.00mm_Vertical
J4: 5V Spare1; JST_PH_B2B-PH-K_1x02_P2.00mm_Vertical
J5, J9: 12V Spare; JST_PH_B2B-PH-K_1x02_P2.00mm_Vertical
J6: IoT_Module; JST_PH_B4B-PH-K_1x04_P2.00mm_Vertical
J7: Pressure; JST_PH_B6B-PH-K_1x06_P2.00mm_Vertical
J8: 5V Spare2; JST_PH_B2B-PH-K_1x02_P2.00mm_Vertical
J10: Spare_A6_A7; JST_PH_B4B-PH-K_1x04_P2.00mm_Vertical
J11: Thermal; JST_PH_B3B-PH-K_1x03_P2.00mm_Vertical
J12: Diff_Flow; JST_PH_B3B-PH-K_1x03_P2.00mm_Vertical
J13: Switch1; JST_PH_B2B-PH-K_1x02_P2.00mm_Vertical
J14: Switch2; JST_PH_B2B-PH-K_1x02_P2.00mm_Vertical
J15: Encoder; JST_PH_B6B-PH-K_1x06_P2.00mm_Vertical
J18: To_Pannel; PinHeader_2x09_P2.54mm_Vertical
K1: SANYOU_SRD_Form_C; Relay_SPDT_SANYOU_SRD_Series_Form_C
Q1, Q2: 1P; SOT-23
R1, R2, R5, R6, R7, R9, R10, R12, R13: 10k; R_0603_1608Metric
R3, R4, R11: 1k; R_0603_1608Metric
U1, U2: AMS1117-5.0; SOT-223-3_TabPin2
U3: LP2985-3.3; SOT-23-5

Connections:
+3V3: C9.1, C12.1, J3.1, J7.1, U3.5 (VOUT)
+12V: C1.1, C4.1, D1.1 (K), J1.1, J5.1, J6.1, J9.1, K1.1, K1.2, U1.3 (VI)
/BTS7960/M+: J15.1; also elsewhere on the board
/BTS7960/M-: J15.6; also elsewhere on the board
/Breathe: J18.3, R2.2; also elsewhere on the board
/Buzzer: R3.2; also elsewhere on the board
/Buzzer-: J18.6, Q1.3 (C)
/CLK_RO: J18.14; also elsewhere on the board
/Cancel: J18.9, R9.2; also elsewhere on the board
/DT_RO: J18.13; also elsewhere on the board
/Diff_Flow: J12.2; also elsewhere on the board
/I2C_SCL: J18.15; also elsewhere on the board
/I2C_SDA: J18.16; also elsewhere on the board
/LED: R11.2; also elsewhere on the board
/N1_A6: J10.3; also elsewhere on the board
/N1_A7: J10.2; also elsewhere on the board
/N1_RX0: J6.2; also elsewhere on the board
/N1_TX0: J6.3; also elsewhere on the board
/N2_D9: J7.2; also elsewhere on the board
/N2_D11: J7.3; also elsewhere on the board
/N2_D12: J7.4; also elsewhere on the board
/N2_D13: J7.5; also elsewhere on the board
/ON_OFF: J18.10, R6.2; also elsewhere on the board
/Relay_Pin: R4.2; also elsewhere on the board
/SW_RO: J18.12; also elsewhere on the board
/Select: J18.11, R7.2; also elsewhere on the board
/Set: J18.8, R10.2; also elsewhere on the board
/Silence: J18.7, R1.2; also elsewhere on the board
/Switch1: J13.1, R12.2; also elsewhere on the board
/Switch2: J14.1, R13.2; also elsewhere on the board
/Thermal: J11.2; also elsewhere on the board
/V_Motor: C2.1, C5.1, K1.3, U2.3 (VI); also elsewhere on the board
/chA: J15.3; also elsewhere on the board
/chB: J15.4; also elsewhere on the board
GND: C1.2, C2.2, C3.2, C4.2, C5.2, C6.2, C7.2, C8.2, C9.2, C10.2, C11.2, C12.2, J1.2, J3.2, J4.2, J5.2, J6.4, J7.6, J8.2, J9.2, J10.4, J11.3, J12.3, J13.2, J14.2, J15.2, J18.2, J18.17, Q1.2 (E), Q2.2 (E), R5.2, U1.1 (GND), U2.1 (GND), U3.2 (GND); also elsewhere on the board
unnamed: D1.2 (A), K1.5, Q2.3 (C)
unnamed: J18.4, R11.1
unnamed: Q1.1 (B), R3.1
unnamed: Q2.1 (B), R4.1, R5.1
VCC_1: C7.1, C10.1, J4.1, J10.1, J18.1, J18.5, R1.1, R2.1, R6.1, R7.1, R9.1, R10.1, U1.2 (VO); also elsewhere on the board
VCC_2: C3.1, C6.1, C8.1, C11.1, J8.1, J11.1, J12.1, J15.5, J18.18, R12.1, R13.1, U2.2 (VO), U3.1 (VIN), U3.3 (ON/~OFF~); also elsewhere on the board

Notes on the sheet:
Regulator 1
Regulator 2
Rotary
Switch
Regulator 3
Motor
Power
To Front Pannel
Sensors
Buzzer

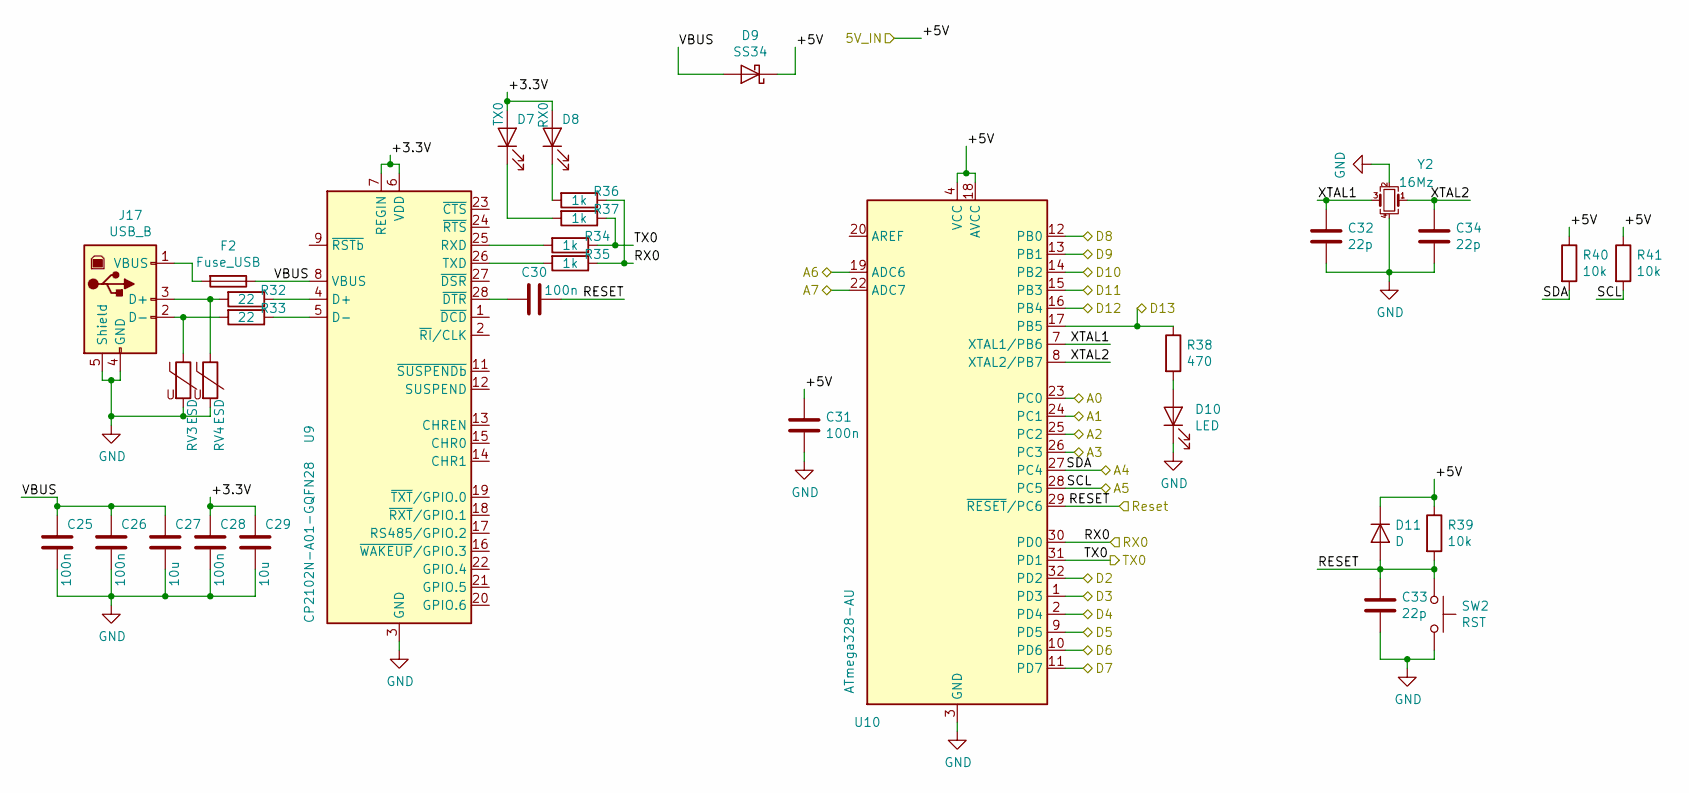
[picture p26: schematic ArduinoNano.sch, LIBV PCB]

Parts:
C13, C14, C16, C18, C19: 100n; C_0603_1608Metric
C15, C17: 10u; C_1206_3216Metric
C20, C21, C22: 22p; C_0603_1608Metric
D2: TX0; LED_0603_1608Metric
D3: RX0; LED_0603_1608Metric
D4: SS34; D_2010_5025Metric
D5: LED; LED_0603_1608Metric
D6: D; D_2010_5025Metric
F1: Fuse_USB; Fuse_1812_4532Metric
J16: USB_B; USB_B_OST_USB-B1HSxx_Horizontal
R14, R15: 22; R_0603_1608Metric
R16, R17, R18, R19: 1k; R_0603_1608Metric
R20: 470; R_0603_1608Metric
R21, R22, R23: 10k; R_0603_1608Metric
RV1, RV2: ESD; D_0603_1608Metric
SW1: RST; Button_Switch_3.2x4.2
U4: CP2102N-A01-GQFN28; QFN-28-1EP_5x5mm_P0.5mm_EP3.35x3.35mm
U5: ATmega328-AU; TQFP-32_7x7mm_P0.8mm
Y1: 16Mz; Crystal_SMD_3225-4Pin_3.2x2.5mm

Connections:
/ArduinoNano1/+3.3V: C16.1, C17.1, D2.2 (A), D3.2 (A), U4.6 (VDD), U4.7 (REGIN)
/ArduinoNano1/A3: U5.26 (PC3)
/ArduinoNano1/Reset: C18.1, C21.1, D6.2 (A), R21.2, SW1.1, U5.29 (~RESET~/PC6)
/ArduinoNano1/VBUS: C13.1, C14.1, C15.1, D4.2 (A), F1.1, U4.8 (VBUS)
/ArduinoNano1/XTAL1: C20.1, U5.7 (XTAL1/PB6), Y1.3
/ArduinoNano1/XTAL2: C22.1, U5.8 (XTAL2/PB7), Y1.1
/Breathe: U5.13 (PB1); also elsewhere on the board
/Buzzer: U5.16 (PB4); also elsewhere on the board
/CLK_RO: U5.32 (PD2); also elsewhere on the board
/Cancel: U5.10 (PD6); also elsewhere on the board
/DT_RO: U5.1 (PD3); also elsewhere on the board
/Diff_Flow: U5.25 (PC2); also elsewhere on the board
/I2C_SCL: R23.2, U5.28 (PC5); also elsewhere on the board
/I2C_SDA: R22.2, U5.27 (PC4); also elsewhere on the board
/LED: R20.1, U5.17 (PB5); also elsewhere on the board
/N1_A6: U5.19 (ADC6); also elsewhere on the board
/N1_A7: U5.22 (ADC7); also elsewhere on the board
/N1_RX0: R17.1, R18.1, U5.30 (PD0); also elsewhere on the board
/N1_TX0: R16.1, R19.1, U5.31 (PD1); also elsewhere on the board
/ON_OFF: U5.12 (PB0); also elsewhere on the board
/Relay_Pin: U5.15 (PB3); also elsewhere on the board
/SW_RO: U5.2 (PD4); also elsewhere on the board
/Select: U5.11 (PD7); also elsewhere on the board
/Set: U5.9 (PD5); also elsewhere on the board
/Silence: U5.14 (PB2); also elsewhere on the board
/Switch1: U5.23 (PC0); also elsewhere on the board
/Switch2: U5.24 (PC1); also elsewhere on the board
GND: C13.2, C14.2, C15.2, C16.2, C17.2, C19.2, C20.2, C21.2, C22.2, D5.1 (K), J16.4 (GND), J16.5 (Shield), RV1.2, RV2.2, SW1.2, U4.3 (GND), U4.29 (GND), U5.3 (GND), U5.5 (GND), U5.21 (GND), Y1.2, Y1.4; also elsewhere on the board
unnamed: C18.2, U4.28 (~DTR)
unnamed: D2.1 (K), R19.2
unnamed: D3.1 (K), R18.2
unnamed: D5.2 (A), R20.2
unnamed: F1.2, J16.1 (VBUS)
unnamed: J16.2 (D-), R15.2, RV1.1
unnamed: J16.3 (D+), R14.2, RV2.1
unnamed: R14.1, U4.4 (D+)
unnamed: R15.1, U4.5 (D-)
unnamed: R16.2, U4.25 (RXD)
unnamed: R17.2, U4.26 (TXD)
VCC_1: C19.1, D4.1 (K), D6.1 (K), R21.1, R22.1, R23.1, U5.4 (VCC), U5.6 (VCC), U5.18 (AVCC); also elsewhere on the board

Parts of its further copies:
C25, C26, C28, C30, C31: 100n; C_0603_1608Metric
C27, C29: 10u; C_1206_3216Metric
C32, C33, C34: 22p; C_0603_1608Metric
D7: TX0; LED_0603_1608Metric
D8: RX0; LED_0603_1608Metric
D9: SS34; D_2010_5025Metric
D10: LED; LED_0603_1608Metric
D11: D; D_2010_5025Metric
F2: Fuse_USB; Fuse_1812_4532Metric
J17: USB_B; USB_B_OST_USB-B1HSxx_Horizontal
R32, R33: 22; R_0603_1608Metric
R34, R35, R36, R37: 1k; R_0603_1608Metric
R38: 470; R_0603_1608Metric
R39, R40, R41: 10k; R_0603_1608Metric
RV3, RV4: ESD; D_0603_1608Metric
SW2: RST; Button_Switch_3.2x4.2
U9: CP2102N-A01-GQFN28; QFN-28-1EP_5x5mm_P0.5mm_EP3.35x3.35mm
U10: ATmega328-AU; TQFP-32_7x7mm_P0.8mm
Y2: 16Mz; Crystal_SMD_3225-4Pin_3.2x2.5mm

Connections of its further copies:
/ArduinoNano2/+3.3V: C28.1, C29.1, D7.2 (A), D8.2 (A), U9.6 (VDD), U9.7 (REGIN)
/ArduinoNano2/A6: U10.19 (ADC6)
/ArduinoNano2/A7: U10.22 (ADC7)
/ArduinoNano2/D4: U10.2 (PD4)
/ArduinoNano2/D7: U10.11 (PD7)
/ArduinoNano2/D8: U10.12 (PB0)
/ArduinoNano2/D10: U10.14 (PB2)
/ArduinoNano2/RX0: R35.1, R36.1, U10.30 (PD0)
/ArduinoNano2/Reset: C30.1, C33.1, D11.2 (A), R39.2, SW2.1, U10.29 (~RESET~/PC6)
/ArduinoNano2/TX0: R34.1, R37.1, U10.31 (PD1)
/ArduinoNano2/VBUS: C25.1, C26.1, C27.1, D9.2 (A), F2.1, U9.8 (VBUS)
/ArduinoNano2/XTAL1: C32.1, U10.7 (XTAL1/PB6), Y2.3
/ArduinoNano2/XTAL2: C34.1, U10.8 (XTAL2/PB7), Y2.1
/Diff_Flow: U10.25 (PC2); also elsewhere on the board
/I2C_SCL: R41.2, U10.28 (PC5); also elsewhere on the board
/I2C_SDA: R40.2, U10.27 (PC4); also elsewhere on the board
/L_PWM: U10.10 (PD6); also elsewhere on the board
/N2_D9: U10.13 (PB1); also elsewhere on the board
/N2_D11: U10.15 (PB3); also elsewhere on the board
/N2_D12: U10.16 (PB4); also elsewhere on the board
/N2_D13: R38.1, U10.17 (PB5); also elsewhere on the board
/R_PWM: U10.9 (PD5); also elsewhere on the board
/Switch1: U10.23 (PC0); also elsewhere on the board
/Switch2: U10.24 (PC1); also elsewhere on the board
/Thermal: U10.26 (PC3); also elsewhere on the board
/chA: U10.32 (PD2); also elsewhere on the board
/chB: U10.1 (PD3); also elsewhere on the board
GND: C25.2, C26.2, C27.2, C28.2, C29.2, C31.2, C32.2, C33.2, C34.2, D10.1 (K), J17.4 (GND), J17.5 (Shield), RV3.2, RV4.2, SW2.2, U9.3 (GND), U9.29 (GND), U10.3 (GND), U10.5 (GND), U10.21 (GND), Y2.2, Y2.4; also elsewhere on the board
unnamed: C30.2, U9.28 (~DTR)
unnamed: D7.1 (K), R37.2
unnamed: D8.1 (K), R36.2
unnamed: D10.2 (A), R38.2
unnamed: F2.2, J17.1 (VBUS)
unnamed: J17.2 (D-), R33.2, RV3.1
unnamed: J17.3 (D+), R32.2, RV4.1
unnamed: R32.1, U9.4 (D+)
unnamed: R33.1, U9.5 (D-)
unnamed: R34.2, U9.25 (RXD)
unnamed: R35.2, U9.26 (TXD)
VCC_2: C31.1, D9.1 (K), D11.1 (K), R39.1, R40.1, R41.1, U10.4 (VCC), U10.6 (VCC), U10.18 (AVCC); also elsewhere on the board

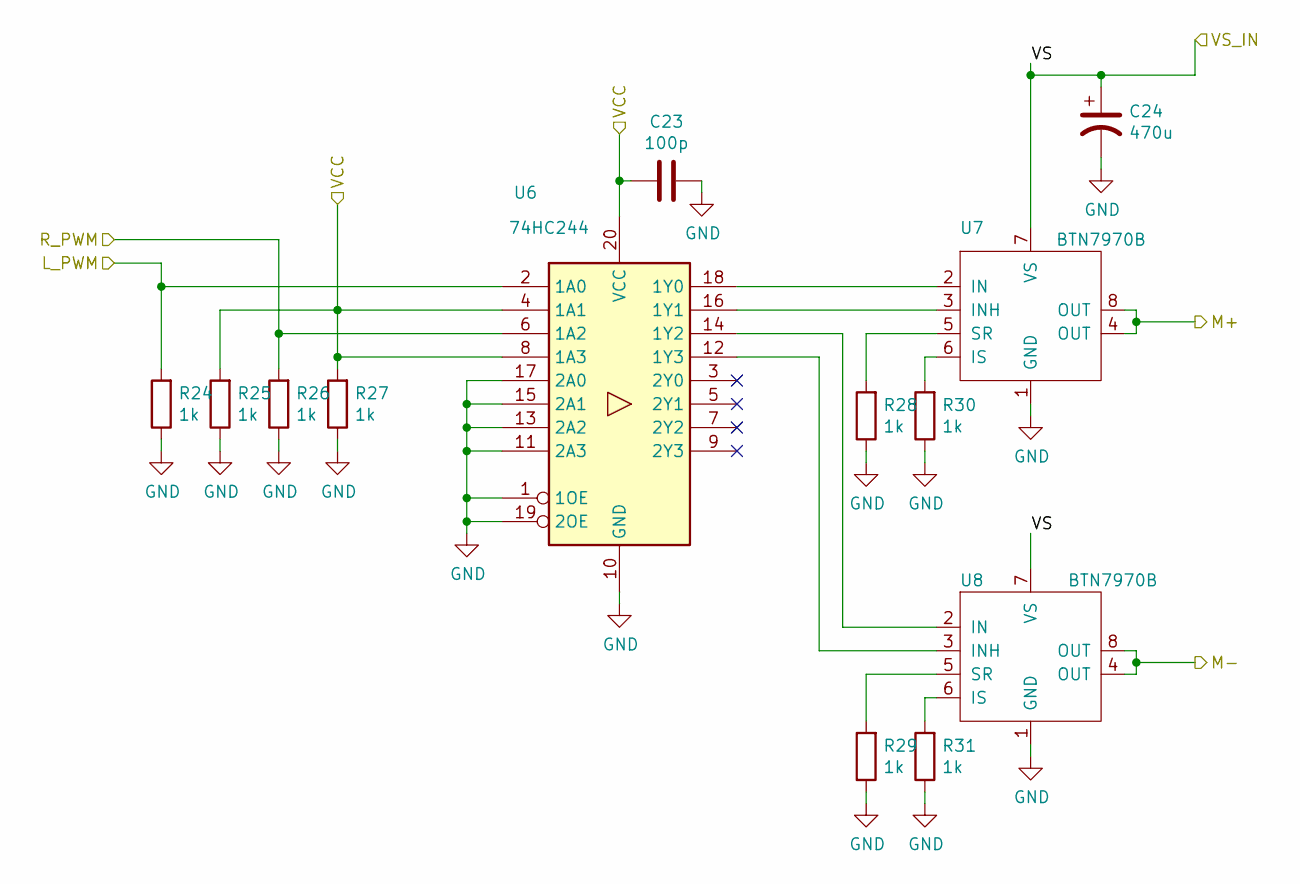
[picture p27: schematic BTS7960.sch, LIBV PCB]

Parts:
C23: 100p; C_0603_1608Metric
C24: 470u; CP_Elec_10x10.5
R24, R25, R26, R27, R28, R29, R30, R31: 1k; R_0603_1608Metric
U6: 74HC244; SO-20_12.8x7.5mm_P1.27mm
U7, U8: BTN7970B; TO-263-7_TabPin8

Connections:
/BTS7960/M+: U7.4 (OUT), U7.8 (OUT); also elsewhere on the board
/BTS7960/M-: U8.4 (OUT), U8.8 (OUT); also elsewhere on the board
/L_PWM: R24.2, U6.2 (1A0); also elsewhere on the board
/R_PWM: R26.2, U6.6 (1A2); also elsewhere on the board
/V_Motor: C24.1, U7.7 (VS), U8.7 (VS); also elsewhere on the board
GND: C23.1, C24.2, R24.1, R25.1, R26.1, R27.1, R28.1, R29.1, R30.1, R31.1, U6.1 (1OE), U6.10 (GND), U6.11 (2A3), U6.13 (2A2), U6.15 (2A1), U6.17 (2A0), U6.19 (2OE), U7.1 (GND), U8.1 (GND); also elsewhere on the board
unnamed: R28.2, U7.5 (SR)
unnamed: R29.2, U8.5 (SR)
unnamed: R30.2, U7.6 (IS)
unnamed: R31.2, U8.6 (IS)
unnamed: U6.12 (1Y3), U8.3 (INH)
unnamed: U6.14 (1Y2), U8.2 (IN)
unnamed: U6.16 (1Y1), U7.3 (INH)
unnamed: U6.18 (1Y0), U7.2 (IN)
VCC_2: C23.2, R25.2, R27.2, U6.4 (1A1), U6.8 (1A3), U6.20 (VCC); also elsewhere on the board

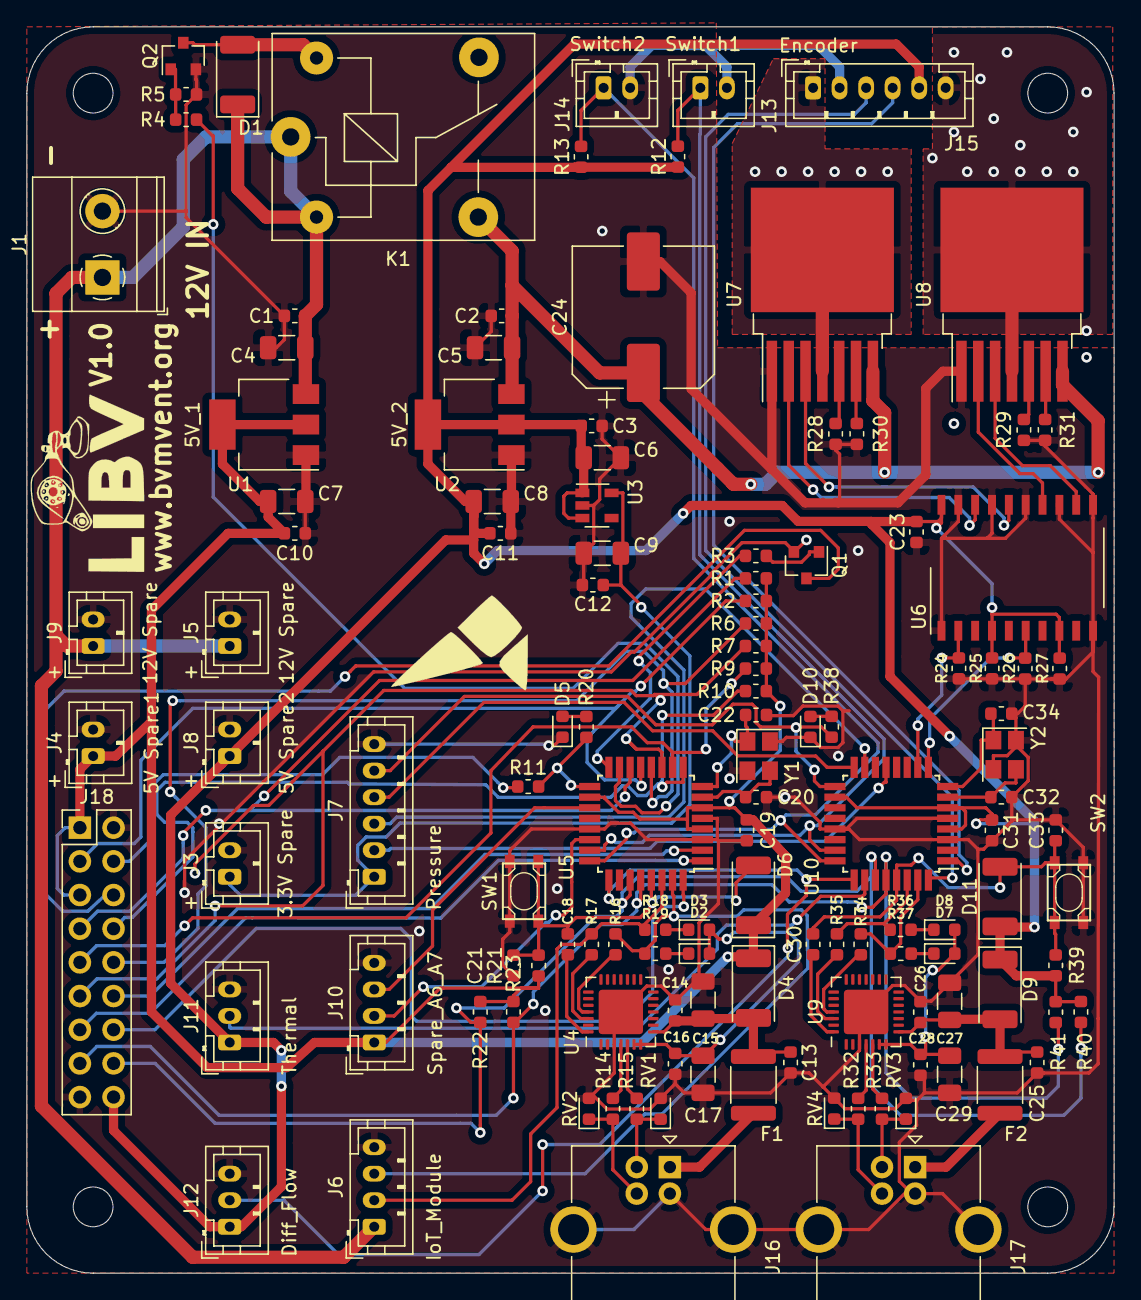
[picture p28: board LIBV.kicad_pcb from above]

Board: 2 copper layers, 82.0 x 94.0 mm, 125 parts (0 on the bottom side), 85 nets.
